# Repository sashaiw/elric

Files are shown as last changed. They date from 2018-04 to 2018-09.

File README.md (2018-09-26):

# elric

The Elric module is intended to be a low-cost, low-commitment myoelectric add-on for the popular open-source e-NABLE Phoenix hand. Its design allows it to easily snap on to the existing gauntlet and be a drop-in replacement for the rail-mounted box. The inexpensive MyoWare sensor can be attached to any muscle on the body for control. An early version of the detailed build instructions can be found in elric_instructions.pdf.

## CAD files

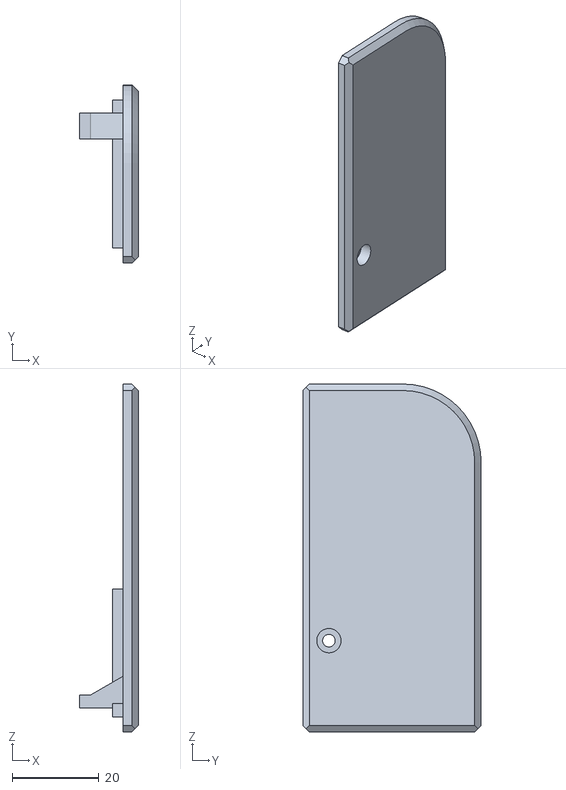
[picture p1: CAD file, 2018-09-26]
lid.STL
13.5 x 41.0 x 80.0

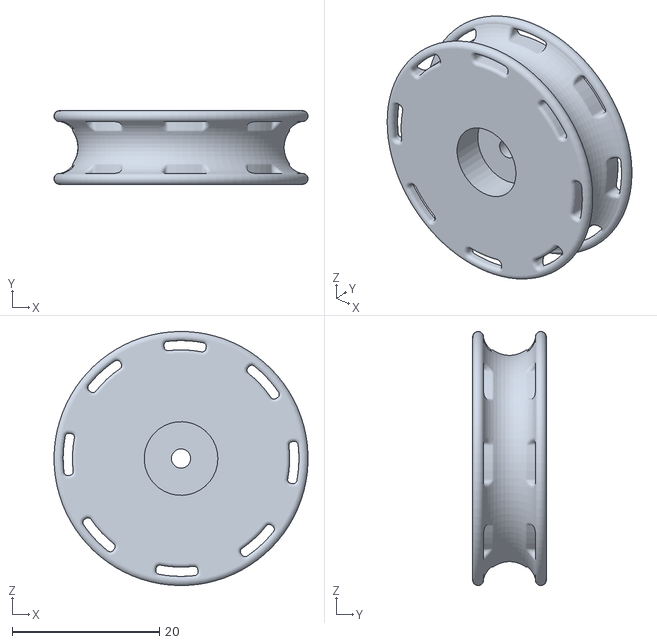
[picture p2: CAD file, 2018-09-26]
spool.STL
34.5 x 10.0 x 34.5

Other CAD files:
enclosure.STL

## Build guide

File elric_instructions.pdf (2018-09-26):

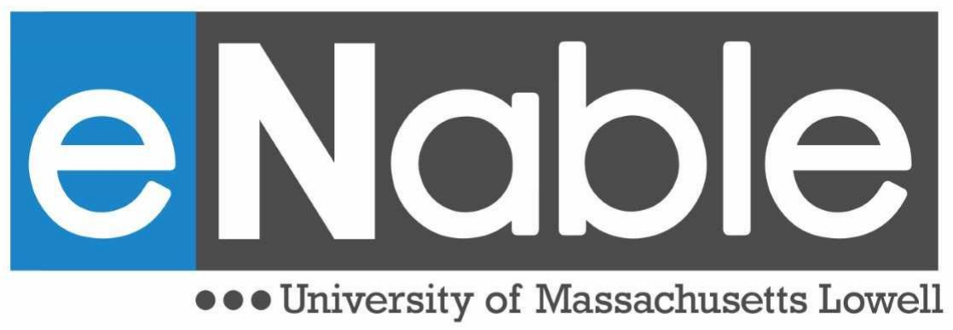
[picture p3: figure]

# How to build an Elric module

Aaron Chen
Vittoria Santoro
Alexander Wilkinson

1

## 1. INTRODUCTION

The Elric module is intended to be a low-cost, low-commitment myoelectric add-on for the popular open-source e-NABLE Phoenix hand. Its design allows it to easily snap on to the existing gauntlet and be a drop-in replacement for the rail-mounted box. The inexpensive MyoWare sensor can be attached to any muscle on the body for control. This guide will walk you through the entire process of assembling, flashing, and using an Elric module.

2

## 2. BUILDING

These instructions assume you have already built a Phoenix hand, for which files and instructions can be found at:

https://www.thingiverse.com/thing:1453190

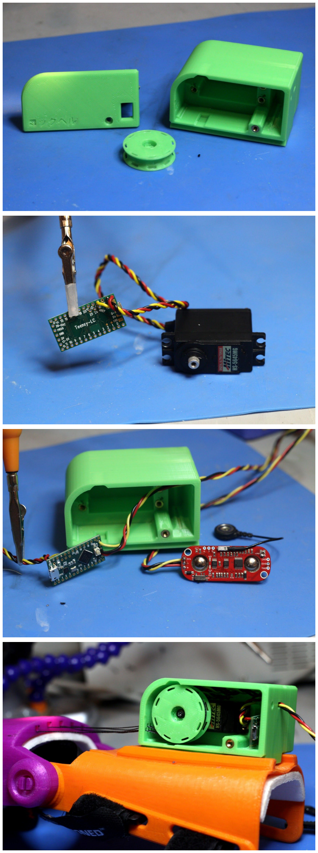
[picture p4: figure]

If you do not plan on using the Phoenix hand as a wrist-actuated device, you do not need to print the gripper box, the device that sits in the rail on the gauntlet. The servo “backpack” will occupy this rail.

Parts list:
- enclosure.stl
- lid.stl
- spool.stl
- 4x M3x0.5 heat-set insert
- 4x M3x0.5x8mm socket head cap machine screws
1. Place heat-set inserts into mounting holes for lid and servo. These can be pressed in with a soldering iron tip that you don’t care about.
2. Solder servo wire to Teensy pins. More info can be found in section 3 - wiring.
3. If you aren’t using a connector, route the MyoWare cable through the hole in the back. Then solder to both Teensy and MyoWare board.
4. Place Teensy board in slot, and screw servo into place.
5. Glue servo horn to spool.
6. Route finger lines to spool, adjust tension by rotating spool inside housing.
7. Screw horn to servo.

3

## 3. WIRING

### PARTS LIST

PART | LINK | Price
Servo | https://www.amazon.com/Hitec-35645S-HS-5645MG-Digital-Torque/dp/B0006O3XLS | $41.98
Teensy LC | https://www.sparkfun.com/products/13305 | $12.95
MyoWare Sensor | https://www.sparkfun.com/products/13723 | $37.95
6MM SMD Button | https://www.sparkfun.com/products/12992 | $0.50
| | Total: $93.38

4

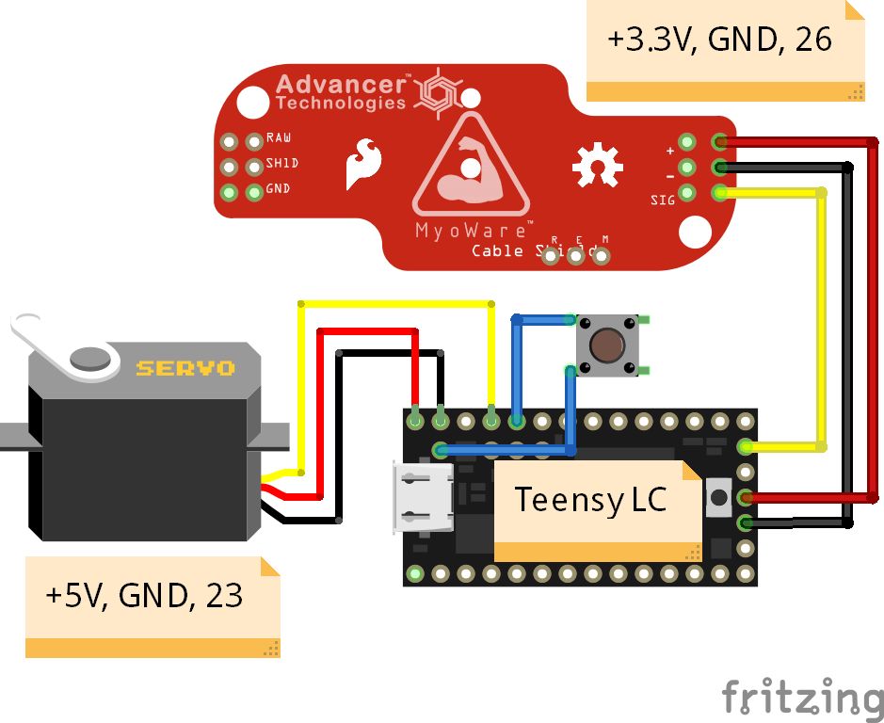
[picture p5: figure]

5

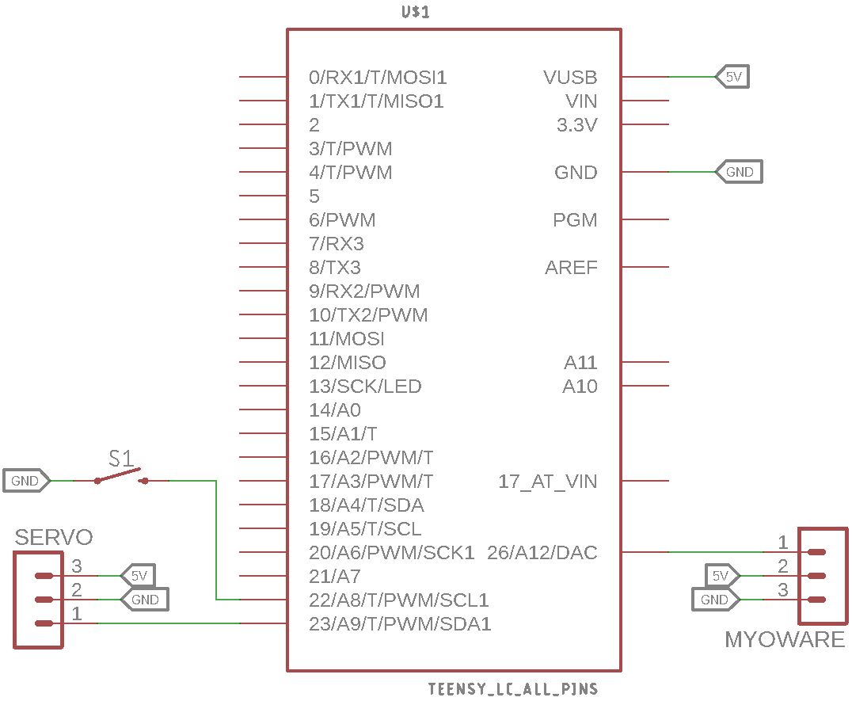
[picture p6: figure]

6

## 4. FLASHING

Now that the circuit is complete, it is time to flash the software onto the Teensy. First, install the necessary software on your computer. We will be installing the Arduino IDE and the Teensyduino add-on. Be sure to follow all installation instructions on each page.

Arduino IDE:
https://www.arduino.cc/en/Main/Software

Teensyduino:
https://www.pjrc.com/teensy/td_download.html

Next, download a copy of the code, or copy and paste it into your Arduino IDE.

Libraries:
Install the following library by cloning or downloading/unzipping in the Arduino/libraries directory:
https://github.com/JonHub/Filters

Elric module code:
https://github.com/sashaiw/elric/blob/master/elric.ino

There are several parameters that you can modify in this code, in case you wish to modify these in the future. Most can be found as variables under the // Tunable parameters comment.

User-tunable parameters
DEFAULT_MIN_INPUT The default minimum sensor value, or the value the sensor reports when the muscle is relaxed

DEFAULT_MAX_INPUT The default maximum sensor value, or the value the sensor reports when the muscle is flexed

RANGE_DELTA The buffering given to the calibrated range to clamp it between a smaller range

CURVE_STEEPNESS The value of s in the equation for the output curve as defined by
f(x) = | tanh(s x | )) 2

1 + 2

1
* ( − 2

1
This curve is used to bias the gripper between fully open/closed to make it easier to use.

FILTER_FREQUENCY Frequency of a low-pass filter applied to the sensor output

7

Under the //pins comment are several variables that represent the pins used on the Teensy. These can be changed, but the defaults will work for the circuit defined in the previous section.

If you don’t feel like modifying the code, don’t worry about it. The defaults will work.
To flash the Teensy, simply connect the board to your computer using a MicroUSB cable and press the Upload button designated by a checkmark in your Arduino IDE. If this is the first time you are uploading Arduino code to your Teensy, press the small button located on your Teensy immediately prior to flashing the code.

8

## 5. USING THE ELRIC MODULE

### Sensor placement

Correct placement of the MyoWare sensor is essential for good performance. The official documentation for the sensor, which can be found here, (https://cdn.sparkfun.com/assets/learn_tutorials/4/9/1/datasheet.pdf) recommends the following steps:

1. Thoroughly clean the intended area
2. Snap electrodes to sensor’s snap connectors
3. Place the sensor on the desired muscle
a. Place the sensor so one of the connected electrodes is in the middle of the muscle body. The other electrode should line up in the direction of muscle length.
b. Peel off backing on electrodes to expose the adhesive and apply them to the skin
c. Place the reference electrode on a bony or nonadjacent muscular part of the body near the targeted muscle

The following image, stolen shamelessly from the MyoWare sensor documentation, illustrates correct sensor placement:

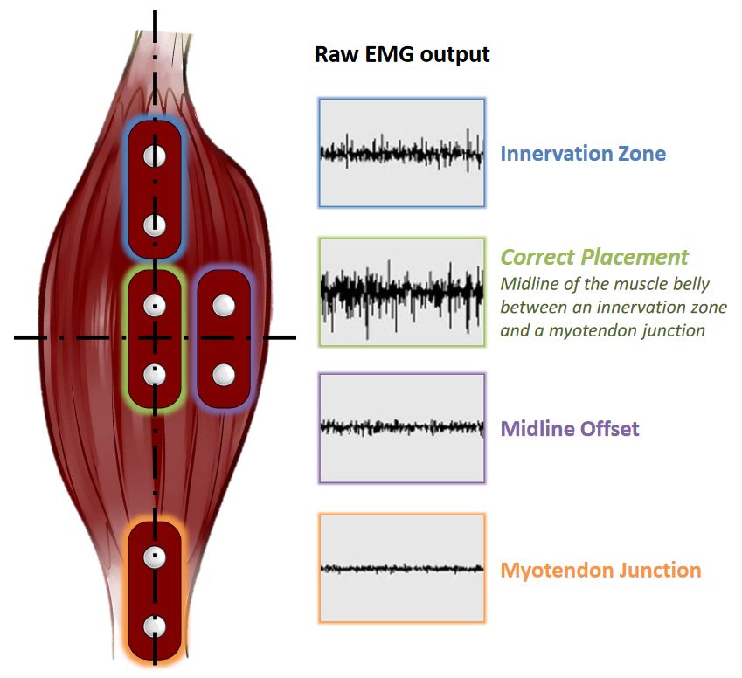
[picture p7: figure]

9

### Calibration

Whenever the sensor is moved or placed on a different person, the device will need to be re-calibrated to set the upper and lower ranges of values being reported by the sensor. The procedure for performing a recalibration is as such:

1. With the device and the sensor connected and powered on, hold the calibration button for 2 seconds. The device should deactivate and the servo should stop moving, indicating that the device is now in calibration mode.
2. With the user’s target muscle relaxed, press the calibration button once. The device will sample the sensor for the next 5 seconds. Afterwards, the device will quickly contract and extend, indicating that this part of the calibration is finished.
3. Press the button again with the user’s muscle fully flexed. The device will sample the sensor again for 5 seconds. When it is finished, it will resume operation.

If you wish to manually change the default calibration, you may edit the code and re-flash the Teensy. See the section about the code for details. It is possible to graph the sensor input and motor output against the minimum and maximum range to be able to set it manually if you enable the serial plotter with the Teensy connected.

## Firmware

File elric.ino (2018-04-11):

#include <Servo.h>
#include <EEPROM.h>
#include <Filters.h>
#include <stdarg.h>

// Tune-able parameters
const int POLL_RATE          = 1;        // Poll rate in ms
const int DEFAULT_MIN_INPUT  = 100;      // Minimum input value (0-1024
const int DEFAULT_MAX_INPUT  = 200;      // Maximum input value (0-1024)
const int RANGE_DELTA        = 25;       // Delta for calibrated range
const int CALIBRATE_LENGTH   = 50;       // Number of values to collect for calibration
const int CALIBRATE_TIME     = 5000;     // Duration (ms) to collect calibration data
const int CURVE_STEEPNESS    = 20;       // Steepness of output curve. DO NOT GO BELOW LIKE 4 OR SOMETHING.
const float FILTER_FREQUENCY = 1;        // Frequency in HZ of LPF

// Pins
const int MOTOR_PIN  = 23; // Servo
const int SENSOR_PIN = 26; // Myoelectric sensor
const int CALIB_BTN  = 22; // Button for calibration routine

// EEPROM addresses
const int MIN_VAL_ADDR = 0;
const int MAX_VAL_ADDR = 0 + sizeof(int);

Servo servo;
FilterOnePole lpf(LOWPASS, FILTER_FREQUENCY);

void setup() {
  Serial.begin(115200);
  servo.attach(MOTOR_PIN);
  pinMode(SENSOR_PIN, INPUT);
  pinMode(CALIB_BTN, INPUT_PULLUP);
}

void loop() {
  float output_value;
  int input_value = analogRead(SENSOR_PIN);
  static int min_input = EEPROM_read_int(MIN_VAL_ADDR);
  static int max_input = EEPROM_read_int(MAX_VAL_ADDR);

  // Calibration buttons
  if (digitalRead(CALIB_BTN) == LOW) {
    calibration_sequence(CALIB_BTN, &min_input, &max_input);
  }

  // Apply LPF
  lpf.input(input_value);
  output_value = lpf.output();

  // Scale to range
  output_value = scale_to_range(output_value, min_input, max_input, 0, 1);

  // Debug, plot two graphs
  debug_graph(4, // Number of arguments
              scale_to_range(input_value, 0, 1024, 0, 1024),
              scale_to_range(output_value, 0, 1, 0, 1024),
              min_input,
              max_input
              );

  // Apply curve
  //output_value = curve(output_value, CURVE_STEEPNESS);

  // Write to servo
  servo.write(180 - scale_to_range(output_value, 0, 1, 0, 180));
  delay(POLL_RATE);
}

float scale_to_range(float input_value, float old_min, float old_max, float new_min, float new_max) {
  return clamp((input_value - old_min) * (new_max - new_min) / (old_max - old_min) + new_min, new_min, new_max);
}

float curve(float x, int steepness) {
  return .5 + .5 * tanh(steepness * (x - .5));
}

void debug_graph(int nArgs, ...) {
    va_list valist;
    va_start(valist, nArgs);
    for (int i=0; i < nArgs - 1; i++) {
        Serial.print(va_arg(valist, int));
        Serial.print(",");
    }
    //Serial.println(va_arg(valist, int));
    va_end(valist);
}

// TODO: Test
//float curve(float x, int k) {
//  w2 = 1 - x;
//  f1 = x;
//  f2 = 0.5 + 0.5 * tanh(s * (x-.5));
//  f = w1 * f1 + w2 * f2;
//}

float clamp(float x, float min_value, float max_value) {
  if (x < min_value) {
    x = min_value;
  }
  if (x > max_value) {
    x = max_value;
  }
  return x;
}

void twitch() {
  servo.write(180);
  delay(200);
  servo.write(0);
  delay(200);
}

void EEPROM_write_int(int ee, int value) {
  const byte* p = (const byte*)(const void*)&value;
  for (unsigned int i = 0; i < sizeof(value); i++) {
    EEPROM.write(ee++, *p++);
  }
}

int EEPROM_read_int(int ee) {
  int value;
  byte* p = (byte*)(void*)&value;
  for (unsigned int i = 0; i < sizeof(value); i++) {
    *p++ = EEPROM.read(ee++);
  }
  return value;
}

void calibration_sequence(int calib_btn, int* min_value, int* max_value) {
  while (analogRead(calib_btn) == LOW) {} // Wait for button press
  *min_value = calibrate_values() + RANGE_DELTA;
  EEPROM_write_int(MIN_VAL_ADDR, *min_value);
  twitch();                   // Signal that calibration is complete.
  while (analogRead(calib_btn) == LOW) {} // Wait for button press
  *max_value = calibrate_values() - RANGE_DELTA;
  EEPROM_write_int(MAX_VAL_ADDR, *max_value);
}

int calibrate_values() {
  Serial.println("CALIBRATING");
  int avg = 0;
  int readings[CALIBRATE_LENGTH];
  for (int i = 0; i < CALIBRATE_LENGTH; i++) {
    readings[i] = analogRead(SENSOR_PIN);
    delay(CALIBRATE_TIME / CALIBRATE_LENGTH);
  }
  for (int i = 0; i < CALIBRATE_LENGTH; i++) {
    avg += readings[i];
  }
  avg /= CALIBRATE_LENGTH;
  return avg;
}

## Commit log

2017-10-06 Fixed bug causing filtering to be borked.
2017-10-10 Now with 20% more filtering!
2017-10-24 Added calibration function
2017-10-27 Calibration un-borked
2018-09-26 Added meshes
    [enclosure.STL, lid.STL, spool.STL]
